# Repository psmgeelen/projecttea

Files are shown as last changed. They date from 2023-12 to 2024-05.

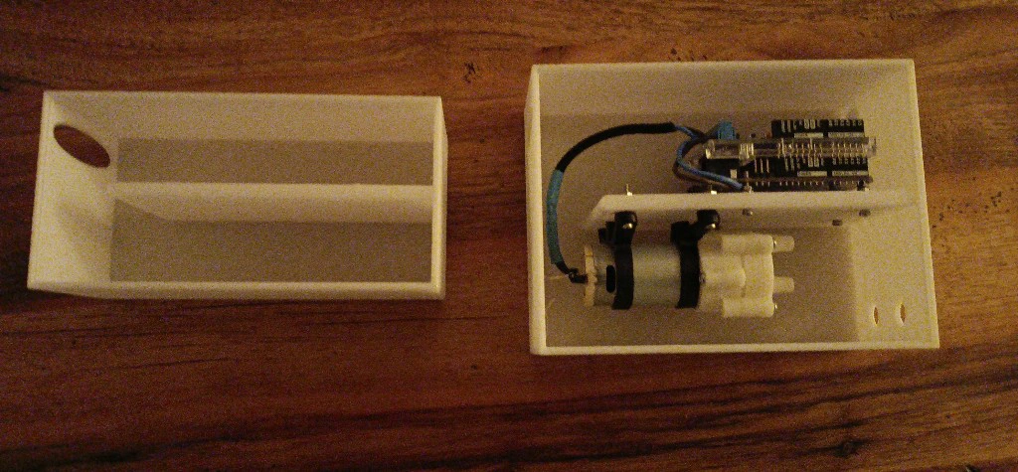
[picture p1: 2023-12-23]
docs/img/temp_image_20231222_074809_28dd540f-97f6-4fa3-9d6f-d0831d5a4639.jpg

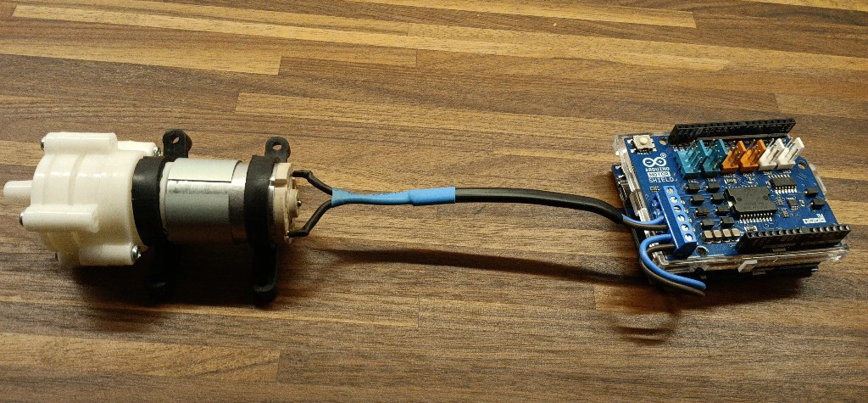
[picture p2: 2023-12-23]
docs/img/temp_image_20231220_173428_03357671-8b48-438e-8a6a-fbaeae2cb090.jpg

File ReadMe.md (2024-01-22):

# Project Tea

Project Tea is an initiative focused on creating an accessible tea-pouring solution for individuals with mobility challenges.

## Featured Articles

1. **Pieter Geelen's Insight:** 
   - [Improving Quality of Life: A Tea Pouring Solution for Anton](https://medium.com/aimonks/improving-quality-of-life-a-tea-pouring-solution-for-anton-e0c595fca284)
   - Explore the physical design and development process of Project Tea through Pieter Geelen’s article.

2. **Anton Mirhorodchenko's Perspective:**
   - [Tea-Tech Journey](https://green-wizard.vercel.app/blog/tea-tech-journey)
   - Discover the story behind Project Tea, including its motivation and software aspects, from Anton's point of view.

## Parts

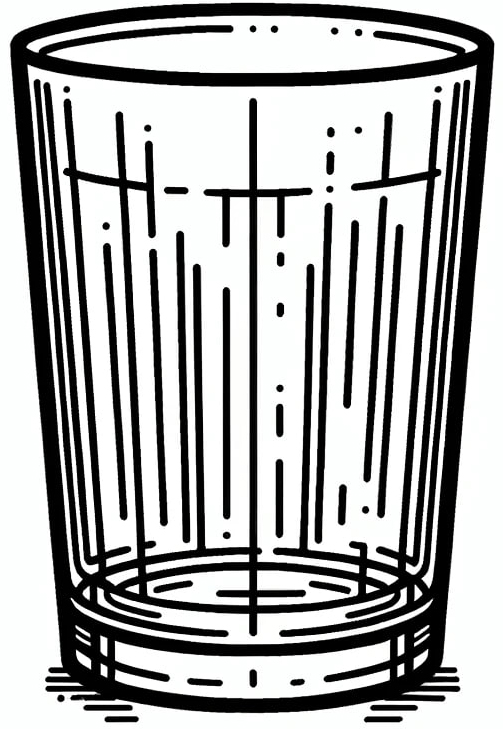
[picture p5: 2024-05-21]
ui/src/components/cup.jpg

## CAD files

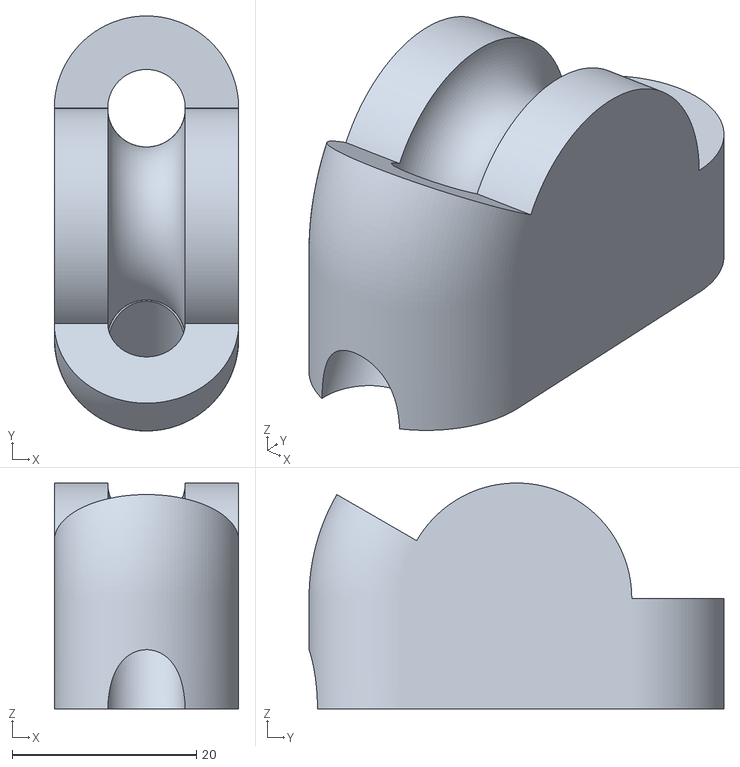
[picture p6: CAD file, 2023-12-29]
3d_models/cupholder_nozzle.stl
20.0 x 45.0 x 24.5

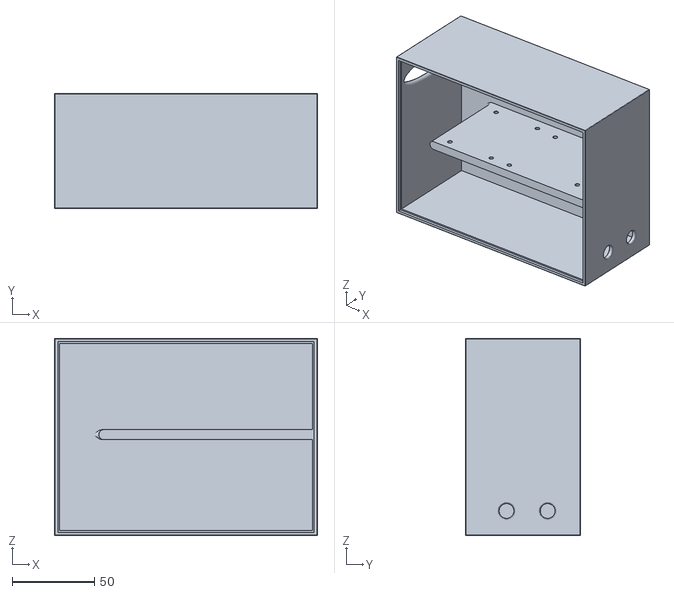
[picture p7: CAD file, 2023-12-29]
3d_models/enclosure_box.stl
160.0 x 70.0 x 120.0

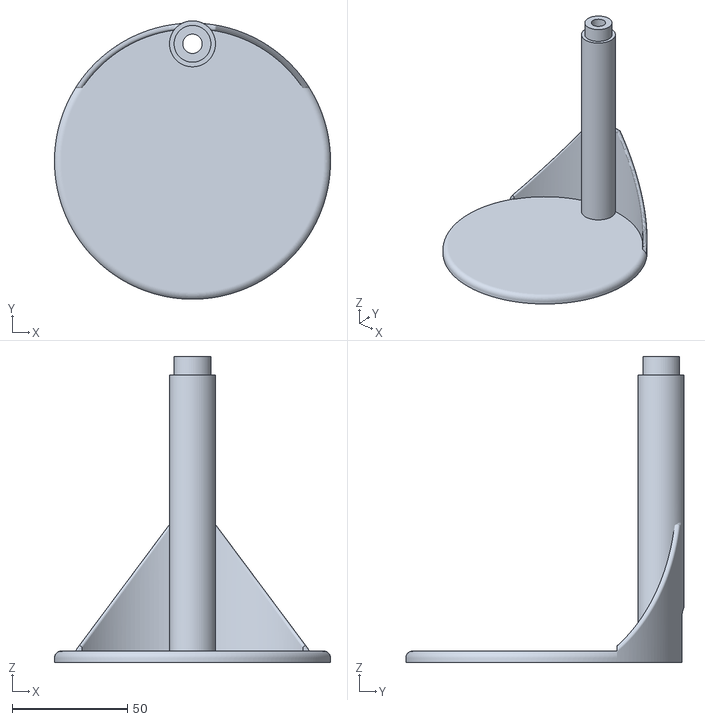
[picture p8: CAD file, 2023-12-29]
3d_models/cupholder_base.stl
120.0 x 121.0 x 133.0

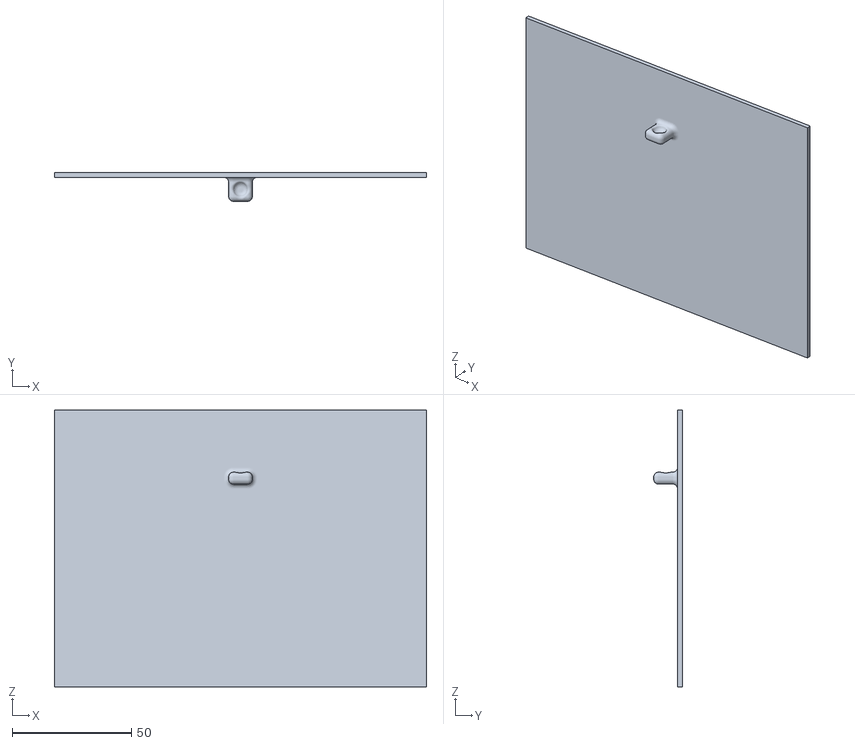
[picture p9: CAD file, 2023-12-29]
3d_models/enclosure_lid.stl
156.0 x 12.0 x 116.0

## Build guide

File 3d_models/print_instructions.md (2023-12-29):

#  3D Models

<!-- TOC -->
* [3D Models](#3d-models)
* [Components](#components)
  * [Main Enclosure](#main-enclosure)
  * [Cupholder](#cupholder)
* [Printing Instructions:](#printing-instructions)
  * [Materials and Equipment](#materials-and-equipment)
  * [Settings](#settings)
  * [Support](#support)
  * [Filament Costs](#filament-costs)
<!-- TOC -->

# Components
The project has 2 main components:
* The main enclosure, that contains the pump and the microcontroller
* A cupholder, to support easier use of the system. 

In the section below you can find both the reasoning and specification of the aforementioned items. Can also skip ahead to the [printing instructions](#printing-instructions).

## Main Enclosure
The main enclosure is designed to contain:
* Arduino Uno Rev 4, Wifi edition
* Arduino Motor shield, that is stacked on top of the Uno
* A small electrical pump

The design leverages a floating "shelve" that has all the components on them. This way we minimize the potential for liquids shortening out electronics. Furthermore it should reduce the overall resonance of the motor, improving quiet operation. The lower 2 holes are for the tubes, that had a diameter of 8 mm. The upper hole is for general access, e.g. if you want to reflash the device.

The Enclosure comes with 2 files:
* enclosure_box.stl
* enclosure_lid.stl

That contain the larger body and a lid to close it off. 

## Cupholder
The cupholder is designed to fascilitate pouring tea into a cup. The design is focussed on having a simple assembly and the least amount of reach into the cup. For this reason the nozzle is angled at 30 degrees to reduce the amount of overhand over the cup, improving access with e.g. a straw. 

The cupholder comes with 2 files:
* cupholder_base.stl
* cupholder_nozzle.stl

The first contains the platform and stem. The nozzle routes the tube towards the cup. Note that for this setup a 8 mm silicone tube was used with inner diameter of 6 mm. The assembly of these part is a simple friction mount of the nozzle on top of the stem. The tube can be route from the back of the base, out and upward of the stem and rounded backdown with the nozzle part. The sequence of assmebly is:
1. Connect Base and Nozzle
2. Route the silicone tubing from the bottom upwards throuch the stem of the base. 
3. Route the remainder, that is coming out of the top of the stem, back into the nozzle part.

The tube should be held in place via simple friction.

# Printing Instructions

## Materials and Equipment

The parts were printed using Transparent PETG filament. Ensure your printing with a Bambu X1 3D printer with a smooth PEI Plate/High Temp Plate. These specific tools were utilized in this process due to their Lidar feature, which is advantageous for this print.

## Settings

Your 3D print settings should be as follows:

- Layer Height: Set your layer height to 0.24 mm. This will determine the quality of your print; smaller values yield higher resolution but take more time.

- First Layer: Set the first layer height to 0.2 mm. This is critical to ensure a good amount of adhesion with the print bed.

- Ironing: Enable ironing for all top surfaces. This option helps in creating a smooth top surface by having the nozzle travel over it a second time.

## Support

Implementing a support structure is vital only for the nozzle for the inside ring that friction mounts to the base. Utilize a tree (auto) type support with the "Tree Strong" style. Further, augment this with 2 layers of rafting to ensure successful print outcomes.

## Filament Costs

Understand the filament use in grams for each component to project your filament costs accurately:

| Part Name         | Filament Cost | Cost in Euros |
|-------------------|---------------|---------------|
| Enclosure, Box    | 126,78 grams  | 3-5 Euros     |
| Enclosure, Lid    | 45,09 grams   | 1-2 Euros     |
| Cupholder, Base   | 57,89 grams   | 1-2 Euros     |
| Cupholder, Nozzle | 7,32 grams    | <1 Euro       |
*\*Assuming that a spool of 1 kg is about 20 to 30 euros*

**Please note:** Times and outcomes may differ based on your specific printer and filament attributes. The above guidelines reflect the settings utilized for this specific print using the Bambu X1 3D printer and Transparent PETG filament.

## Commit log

2023-12-26 adding 3d models and some notes.
    [cupholder_base.stl, cupholder_nozzle.stl, enclosure_box.stl, enclosure_lid.stl]
2023-12-29 remove local and attempt to switch to unity framework
2024-01-30 impl. power level control in UI
2024-01-30 basic impl. of power control
